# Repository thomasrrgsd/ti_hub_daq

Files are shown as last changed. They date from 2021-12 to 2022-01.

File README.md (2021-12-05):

<h1 align="center">TI Innovator HUB Data Aquisition Tool<br/>Team TI-82<br/>Cameron Dennis, John Douthit, William Jarratt, Christian Offodile</h1>

## Table of Contents

* [Introduction](#introduction)
* [User Guide and Theory of Operation](#user-guide-and-theory-of-operation)
* [Folder Descriptions](#folder-descriptions)
* [Demonstration Videos](#demonstration-videos)
* [Project Pitch](#project-pitch)

## Introduction

### Background
Students often begin learning about electronics in an environment where there is no access to the needed equipment, such as oscilloscopes, logic analyzers, function generators, and multimeters.

### Objective
Our goal was to create an inexpensive add-on for the TI Innovator HUB that provides data acquisition capabilities, with an intuitive web page based graphical user interface that works across many user devices.

### Product Requirements
- 8 Channel logic analyzer
- DMM that measures current, voltage, power, resistance
- 2 Channel oscilloscope
- Sine, square, sawtooth function generator
- Web browser-based GUI
- Wi-Fi Connectivity

### Design Challenges Encountered
- Integrating firmware for each peripheral.
- Optimizing data stream for real time operation.
- Changing firmware to allow peripherals to communicate with each other.
- Improving error checking to prevent hangups.

##  User Guide and Theory of Operation

Please see [this folder](./project_files/).

## Folder Descriptions

- /esp32_firmware: This folder gives the rundown on the wifi module (ESP32). Contains the firmware and instructions on how to upload it to the ESP32 and run it with the TI Innovator HUB.
- /final_gui: This folder shows the code behind the web based GUI. This folder contains instructions on how you can modify the webpages, encode them, and update them on the ESP32.
- /project_files: This folder contains administrative documents such as BOM, budget, project planning, theory of operation, and user manual. It is important to note that how to use the project and how it works is contained in the documents in this folder.
- /schematics: This folder contains the CAD files used to create the PCBs for each module. The PCBs were designed using EagleCAD.
- /ti_innovator_hub_firmware: This folder contains information on the firmware that resides inside the TI Innovator HUB. How the software works is located in the theory of operation document.

## Demonstration Videos

- [Beta Demo Video](https://youtu.be/WWzbL9Egt7U)
- [Final Demo Video](https://www.youtube.com/watch?v=TzPDwndSMNo)

## Project Pitch

### Background of Company: 
Global semiconductor company that designs, manufactures, tests and sells analog and embedded processing chips. Our products help our customers efficiently manage power, accurately sense and transmit data and provide the core control or processing in their designs.

### Problem Background and the need:
Work on building a basic instrumentation tool for portable signal measurements using the classroom ready TI-Innovator Hub product. Create a basic oscilloscope out of a microcontroller for collecting test and measurement data! Over the course of the project, the team will use an existing microcontroller kit and create a GUI interface to showcase wave forms, logic analyzer data, and digital multimeter functions. It is very important for engineers to be able to take measurements when debugging hardware. While benchtop equipment is highly capable, it is not portable and can be very expensive. The best tools are often the ones that are available, so portable tools are always in demand, even if the performance is not the same as professional equipment. The team will create software that works with existing hardware to display information collected from the portable data acquisition tool. They will iterate the design to improve the user “out of box” experience. They will use Whole Product development philosophy to create the necessary marketing materials and software examples to ensure a positive experience with users. The team will also design or research any accessory components that will be included in the final kit, which could include a custom enclosure, connectors, cables, power supplies, stickers, and other necessary parts.

### Problem Description/requirements (List of high-level functionality you expect to see in the end product):
- Software GUI that runs in web browser or as native PC application
- GUI Composer app or HTML5 app
- Functional prototype
- TI-Innovator Hub
- Jumper Wires
- (optional) Additional sensors or peripherals (e.g. DAC, voltmeter)
- (optional) Measurement probes or scope probes
- Programmable by USB from host PC
- Test plan to verify use for academic settings
- Identify and test use cases for basic circuits
- Documentation on user manual and quick start guide
- Include pin map diagram for inputs
- Include color photo of final board
- Explanation of out of box demo or default program
- At least 1 example code samples with documentation
- Measurements displayed in GUI
- Can be based on TI code examples provided for MCU or other sources
- Make available for Code Composer Studio and/or Arduino IDE
- Written list or physical prototypes of accessories for the development board which could include a custom enclosure, connectors, cables, power supplies, stickers, and other necessary parts

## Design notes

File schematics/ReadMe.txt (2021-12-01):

List of Files in Folder
* FUNCGEN (Function Generator hardware files)
   * FUNCGENSCH.png (Image of schematic)
   * FUNCGENBRD (Image of board layout)
   * PCB_TI82_FuncGen.zip (Gerber files)
   * TI_DAC_PCB (Eagle design files)
      * TI_DAC5V.brd (Board design file)
      * TI_DAC5V.sch (Schematic design file)
* ESPPCB1 (Wifi Module hardware files 1st iteration)
   * ESPSCH1.png (Image of schematic)
   * ESPPCB1.png (Image of board layout)
   * PCB_TI82_ESP1.zip (Gerber files)
   * TI_ESP_PCB (Eagle design files)
      * TI_ESP_PCB.brd (Board design file)
      * TI_ESP_PCB.sch (Schematic design file)
* ESPPCB2 (Wifi Module hardware files 2nd iteration)
   * ESPSCH2.png (Image of schematic)
   * ESPPCB2.png (Image of board layout)
   * PCB_TI82_ESP2.zip (Gerber files)
   * TI_ESP_PCB2 (Eagle design files)
      * TI_ESP_PCB2.brd (Board design file)
      * TI_ESP_PCB2.sch (Schematic design file)
* MULTIMETER
   * DMMSCH (Image of schematic)
   * DMMPCB (Image of board layout)
   * PCB_TI82_DMM.zip (Gerber files)
   * TI_DMM_PCB (Eagle design files)
      * TI_DMM_PCB.brd (Board design file)
      * TI_DMM_PCB.sch (Schematic design file)

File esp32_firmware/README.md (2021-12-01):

# Wifi Module (ESP32-WROOM-32D)

## Table of Contents

* [Introduction](#introduction)
* [Software](#software)
* [Hardware](#hardware)
* [How to Program using USB to TTL](#how-to-program-using-usb-to-ttl)
* [Bugs and To Do](#bugs-and-to-do)

## Introduction

The wifi Module is connected to the TI Innovator HUB using a grove cable and host the graphical user interface that the user uses from their device. The wifi module communicates over the grove cable using UART at 4Mbps. The GUI sends commands and receives data from the wifi module through 2 websockets. Websocket 1 is for commands from GUI to wifi modules and websocket 2 is for data from wifi module to GUI. The commands received from the GUI are forwarded over UART to the TI Innovator HUB. The data that is sent to the GUI comes from the TI Innovator HUB via UART.

Wifi Module High Level

## Software

The firmware was produced using the Arduino IDE. The ESP32 package may need to be installed, [Install ESP package in Arduino](https://docs.espressif.com/projects/arduino-esp32/en/latest/installing.html). The software utilizes the AsyncTCP and ESPAsyncWebServer packages that can be found at [ESPAsyncWebServer](https://github.com/me-no-dev/ESPAsyncWebServer) and [AsyncTCP github](https://github.com/me-no-dev/AsyncTCP).

The firmware can be broken down into a few parts:

1. Webpage GZIP encoded binary arrays. These can be found from line 29 to line 43 (line numbers could change). The creation of these binary arrays can found in the final_gui directory. These arrays contain the complete set of GUI information needed by the webbrowser.
2. Setup and initialization of the Async Server and websocket. The tcp server and websockets are configured to response to certain http request. Each webpage and dependency is routed to a certain http request and is configured to be transmitted using GZIP encoding. The websockets are configured to responde to certain URLs on ports 80 and 81. Also, how the websockets respond to an event is configured in onEvent and onEvent2. The websocket responses are simply to forward data to either the TI Innovator HUB or to the GUI.
3. Loop function. Inside this function, the wifi module monitors UART channel 2 for incoming data from the TI Innovator HUB. When data is found, and both websockets are open, then the HandleDataPacket function is called to handle the incoming data from the TI Innovator HUB. This data is sent to the webpage GUI through websocket 2.

## Hardware

The wifi module uses an ESP32-WROOM-32D on a customized PCB that was designed by Christian Offodile. The PCB pictured below is an earlier revision but maintains similar functionality to our final PCB design. For more information on the final PCB iteration, please look into the schematics directory. 

A.  This 2x3 male header is used by the ESP programmer [ESP-Prog-Board](https://docs.espressif.com/projects/espressif-esp-iot-solution/en/latest/hw-reference/ESP-Prog_guide.html). Alternatively, this header can be used with the pushbuttons to program the ESP32 using a USB to TTYL converter [Example](https://www.amazon.com/gp/product/B07WX2DSVB/ref=ppx_yo_dt_b_asin_title_o01_s00?ie=UTF8&psc=1).

B.  This grove connector is used to connect the Wifi PCB to the TI-Innovator HUB. The connector provides power and a connection to UART2 RX and TX.

C.  These LEDs are from top to bottom: Amber (GPIO 23), Red (GPIO 22), and Green (GPIO 21).

D.  This 3 pin male header is used to choose which power source is to be used. The jumper on the bottom 2 pins is for the programmer supplying power. The top 2 pins are for the grove connector to the TI-Innovator HUB.

E.  These 2 pushbuttons are used to pull the EN and GPIO1 low. EN and GPIO1 are normally pulled high via a pull up resistor. Pulling EN and GPIO-0 low is required to download the firmware if not using the ESP-Prog-Board, or any other programmer that has extra circuitry available to pull the EN and GPIO1 pins low. The pushbuttons were introduced to allow for wider compatibility with programmers.

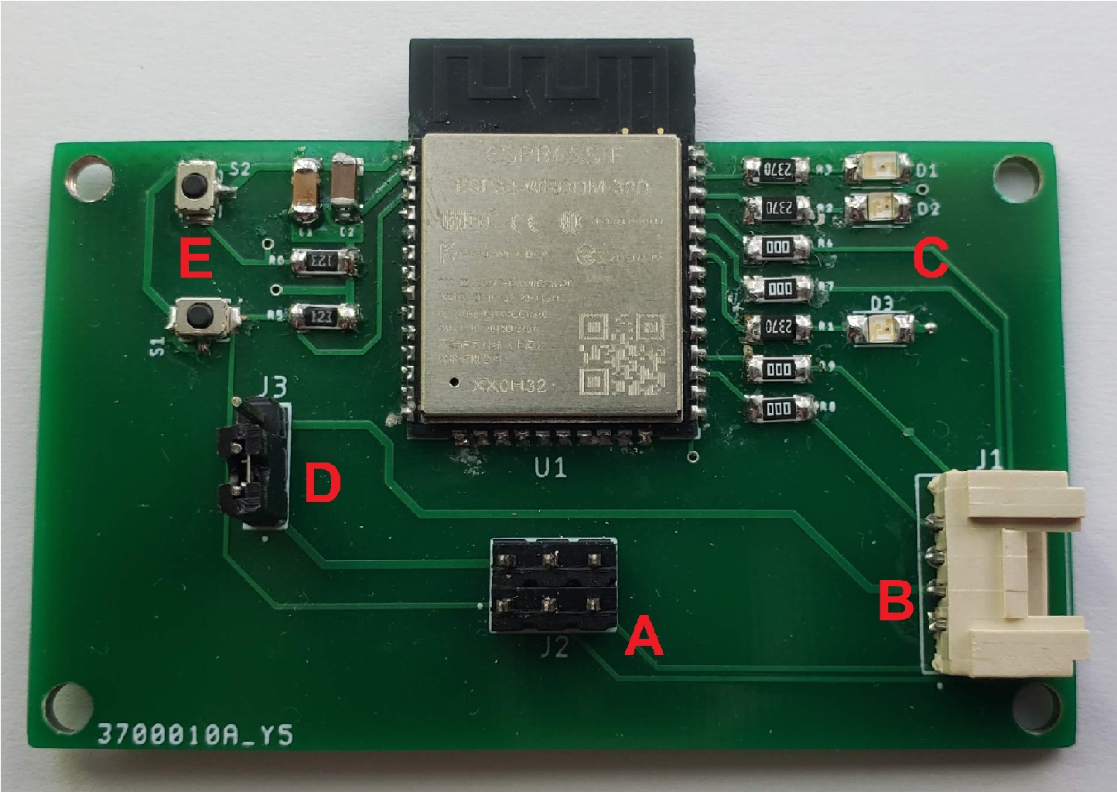
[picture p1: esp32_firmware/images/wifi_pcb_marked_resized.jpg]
wifi_pcb


## How to Program Using USB to TTL

### **Some programmers can be configured for 5v. Ensure that it is not set to 5v. The PCB does not step down the voltage.**

These steps are for those who are using a USB to TTL programmer that does not have a circuit available for pulling EN and GPIO1 low.

1. Arduino IDE and programmer are installed and configured. Arduino has all necessary dependencies installed and programmer has drivers installed.
2. Close any application on your computer that uses the USB to TTL programmer. The UART channel 0 cannot be shared.
3. Apply power (3v3) to the ESP32 via a power source that can provide > 250 mA @ 3v3. The TI Innovator HUB has 3v3 available with max amperage of 500 mA available on the breadboard.
4. Connect ESP32 UART0 TX to programmer RX, connect ESP32 UART0 RX to programmer TX.
5. Ensure that programmer and ESP32 share the same ground reference. Connect programmer ground to ESP32 ground.
6. Determine which COM port the programmer uses and set the Arduino IDE to use that COM port.
7. Begin upload of sketch to ESP32 from Arduino IDE. You will see a message showing that the Arduino IDE is trying to program the ESP32. You will see "___...". At this point you must press the pushbotton that pulls GPIO1 low. Hold that pushbutton until the download begins.
8. Once the download has finished, press the pushbotton that pulls EN low to reset the ESP32. 
9. Once the ESP32 is reset it should begin running the firmware downloaded to it.

Note: You can use a serial terminal, such as [Tera Term](https://ttssh2.osdn.jp/index.html.en) to view what is happening on UART channel 0 using the USB to TTL programmer, while you are not downloading firmwares. For example, if you hold GPIO1 low and press reset, you will see in the serial terminal that the ESP32 goes into serial bootloader mode.

## Bugs and To Do

### To Do
- Add admin page: We want the user to be able to set the SSID and password among other properties. These properties can be stored in static memory and kept after power down and reset.
- Add randomized SSID: Because there will be multiple devices running, the SSIDs cannot collide and so we can use the ESP32 unique MAC address to achieve this.
- Increase operation robustness: As of now, the wifi module operates well, and most hangups result from the TI Innovator HUB. However, the ESP32 has cpu resources that could be dedicated to error checking and handling to help with hangups caused anywhere in the data streaming pipeline.

### Bugs
- The websocket hangs up and quick data speeds. It is suspected that this may have something to do with the buffer. Making the device operation more robust would include adding ways of checking and handling buffer overflow.

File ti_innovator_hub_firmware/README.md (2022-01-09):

# TI Innovator HUB Firmware (MSP432P401R)

## Table of Contents

* [Introduction](#introduction)
* [Software](#software)
* [Hardware](#hardware)
* [Bugs and To Do](#bugs-and-to-do)

## Introduction

The TI Innovator HUB is the center of this project. Each module connects to the HUB through its many grove ports described in the [Hardware](#hardware) section. When the HUB is powered on, it intializes all its peripherals and configures the multimeter. Then it runs in a loop where it waits for incoming serial data from the wifi module. When a command is given, the HUB responds. When a module is turned on (e.g. Oscilloscope), then the data is recorded and turned into a data packet. This data packet is updated and sent out to the wifi module repeatedly in the loop. The HUB is always communicating with the wifi module, but if nobody is connected to the wifi, then the data is just dumped in the wifi module.

## Software

The firmware for the TI Innovator HUB was written with Code Composer Studio (CCS) 10.4. This project uses software abstraction layers from the driverlib package. The project requires [driverlib](https://www.ti.com/tool/MSPDRIVERLIB) to run. Addtionally, the TI Innovator HUB contains an MSP432P401R and so in order to flash the HUB, you must have the MSP432 drivers installed.
It is intended that the CCS project files will be converted into a TI Innovator HUB sketch in the future to allow flashing with the sketch using the appropriate tool. The firmware utilizes many of the HUBs internal peripherals to perform its functions. The UART, I2C, DMA, ADC, TIMER_A, and Interrupt vectors are used. The theory of operation is not covered here, but is instead found in the [project_files folder](https://github.com/thomasrrgsd/ti_hub_daq/tree/main/project_files).

## Hardware

The TI Innovator HUB has an MSP432P401R inside of it and this was used to prototype the TI Innovator HUB DAQ. The TI Innovator HUB documentation specifies how the port pins are mapped to the external connectors. The pin mappings are given below in addition with there function with regard to the project:
- IN1 / P5.4 and P5.5 / Not used
- IN2 / P4.5 and P4.7 / A8 and A6 (Oscilloscope ch 2 and 1 respectively)
- IN3 / P4.4 / Not used
- OUT1 / P3.2 and P3.3 / Wifi module UART RX and TX
- OUT2 / P3.5 and P3.7 / Not used
- OUT3 / Power input for wifi module
- I2C / P6.4 and P6.5 / Multimeter and Function Generator
- Breadboard / {P2.6, P2.4, P2.7, P5.1, P5.2, P5.0, P3.0, P1.5, P1.6, P1.7} / Logic Analyzer channels 1-8.

Additionally, you can look at the firmware to see which pins are mapped to which device.

## Bugs and To Do

### To Do
- Fix magic numbers: There are numbers in the code that represent something but are not obvious do to not using obvious names.
- Update variable types to uint8_t and uint16_t, etc: For uniformity and also to make sure that code is compatible between different devices if needed. Only important in the case where a variable, such as int is a different size on different devices.
- Increase robustness of firmware: The firmware doesn't operate as efficient as it could. Some areas of code rely on time delays. There are bugs that can hang up the system and requires a restart. Some issues can be solved by implementing more error checking to increase robustness.
- Increase modularity and minimize use of global variables: We want each peripheral and module to have its own .c and .h file. This provides a nice API that abstracts and simplifies coding as the project becomes more complex (it got very complex). Additionally, not protecting code and using bad practices, such as global variables can easily cause or be the cause of bugs due to uncoordinated access to a global variable.
- Switch firmware to RTOS: Right now we have to use delays to make the modules operate together. A robust system for coordinating operation is needed. This can be best provided by an RTOS.
- Change I2C to DMA: Interrupts introduce tremendous overhead. This is a significant overhead with regards to the function generator.

### Bugs

- Without a delay after initialization in main, the firmware does not operate correctly when not in debug mode. Most likely due to the I2C not being ready before initializing the multimeter directly after enabling interrupts.
- When receiving serial data (command packet) on UART2 RX, sometimes the data will be dropped and hangup the serial data stream. This began happening when the baud rate was increased to 4Mbps. We knew that raising the baud this high would introduce errors and there is no existing system to account for this error. This is one major reason for using time delays to send information. Ideally, the GUI or ESP32 would notify the MSP432 when it can send its next data, but every so often it hangs up without error checking. On a period delay, if data is missed, then it just keeps going.
- Multimeter and Function Generator must be plugged into I2C for the project to work. This is due to using a while loop with the multimeter and function generator I2C code that looks for a successful transmit. If the transmit does not succeed, then the program hangs up. There are better ways to implement this system and we just did not have time to get around to it.

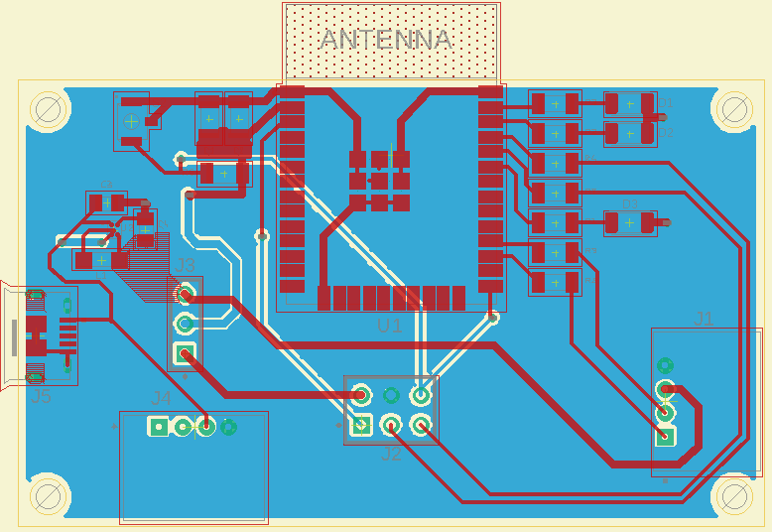
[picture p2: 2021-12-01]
schematics/ESPPCB2/ESPPCB2.png

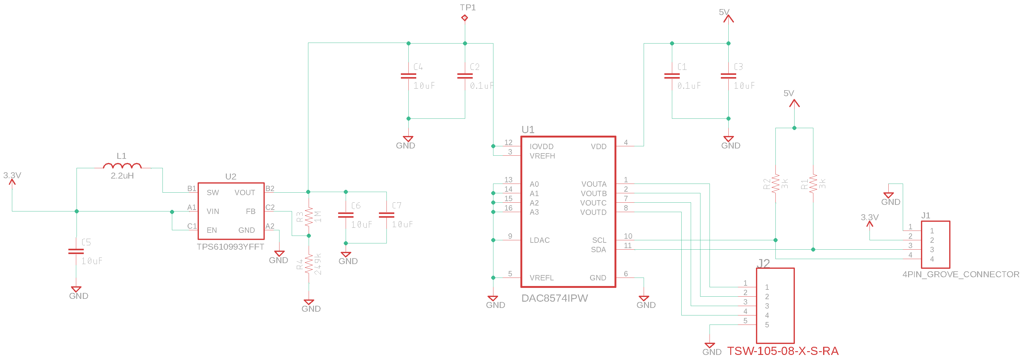
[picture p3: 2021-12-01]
schematics/FUNCGEN/FUNCGENSCH.png

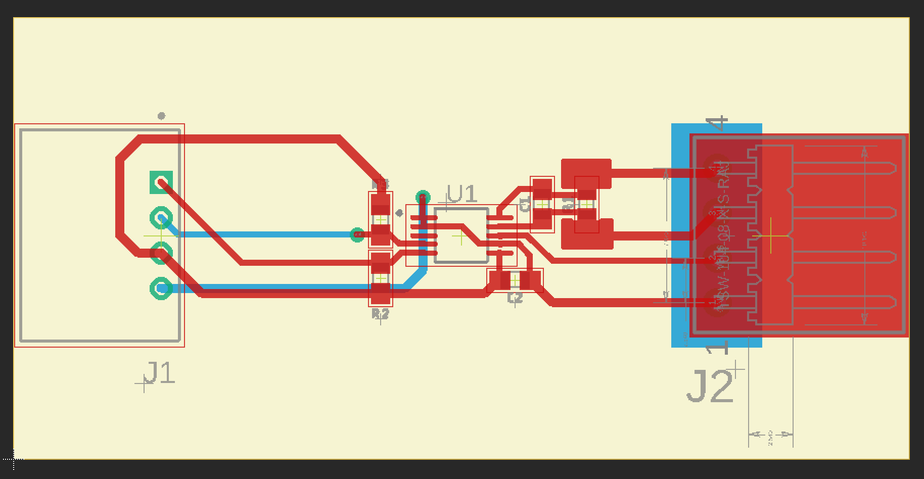
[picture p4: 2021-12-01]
schematics/MULTIMETER/DMMPCB.png

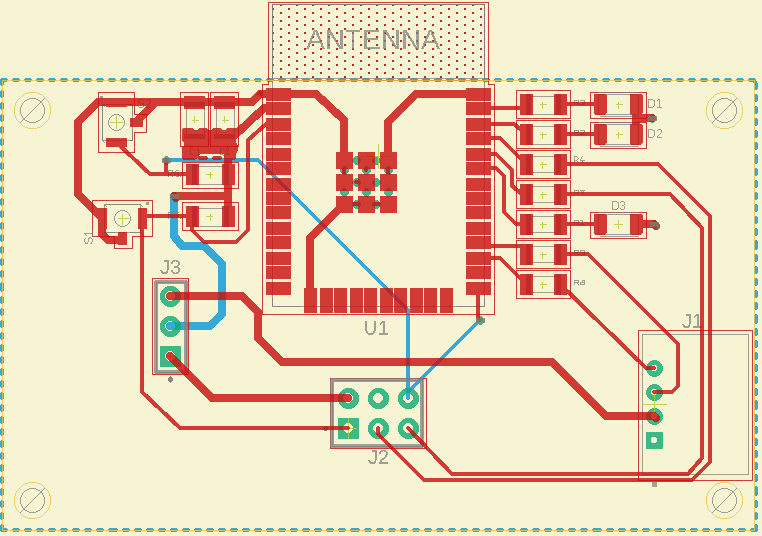
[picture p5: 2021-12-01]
schematics/ESPPCB1/ESPPCB1.png

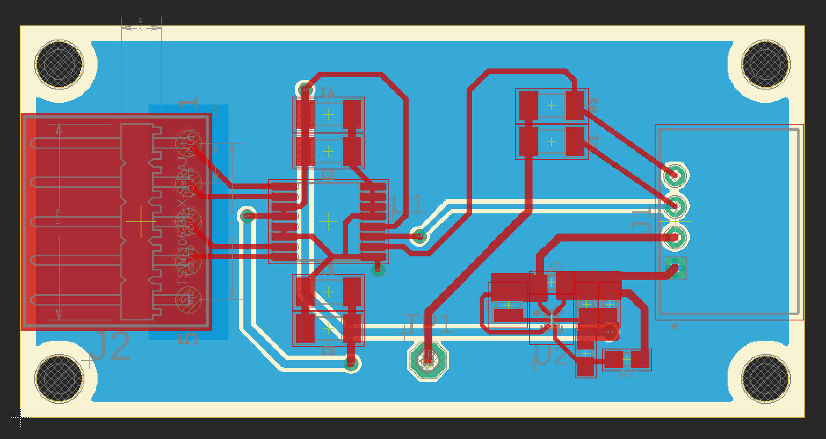
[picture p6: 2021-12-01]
schematics/FUNCGEN/FUNCGENBRD.png

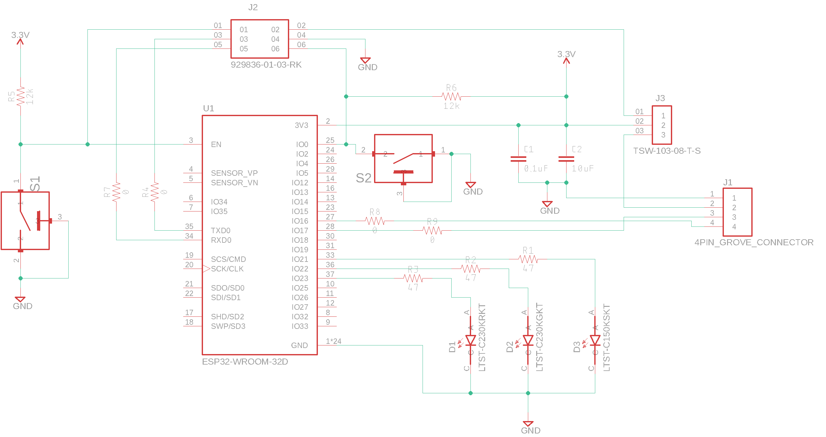
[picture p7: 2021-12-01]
schematics/ESPPCB1/ESPSCH1.png

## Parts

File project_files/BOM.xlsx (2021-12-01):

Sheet: BOM
Function Generator Parts List
QUANTITY | MANUFACTURER PART NUMBER | COMMENT | DESIGNATOR | FOOTPRINT | UNIT PRICE ($) | EXTENDED PRICE ($) | NOTES
1 | TSW-105-08-T-S-RA (https://www.digikey.com/en/products/detail/TSW-105-08-T-S-RA/SAM1051-05-ND/1102419?itemSeq=380598215) | CONN HEADER R/A 5POS 2.54MM | J2 | -- | 0.42 | 0.42
1 | 114020163 (https://www.digikey.com/en/products/detail/seeed-technology-co.,-ltd/114020163/12323560) | Grove Series Connector 20 Pack | J1 | -- | 3.2 | 3.2
2 | C1206C104K8RAC7800 (https://www.digikey.com/en/products/detail/kemet/C1206C104K8RAC7800/2215080?s=N4IgTCBcDaIMIEYwAYBsjkBYDSAOASgIJwDsuyyIAugL5A) | CAP CER 0.1UF 10V X7R 1206 | C1, C2 | 1206 | 0.45 | 0.9
2 | C1206C106K8PACTU (https://www.digikey.com/en/products/detail/kemet/C1206C106K8PAC7800/2215117?s=N4IgTCBcDaIMIEYwAYBsi0GkAcAFAgnACoCqIAugL5A) | CAP CER 10UF 10V X5R 1206 | C3, C4 | 1206 | 0.36 | 0.72
2 | GRM188R60J106ME47J (https://www.digikey.com/en/products/detail/GRM188R60J106ME47J/490-6405-1-ND/3845602?itemSeq=375936658) | CAP CER 10UF 6.3V X5R 0603 |  | 603 | 0.37 | 0.74
2 | ERJ-8GEYJ302V (https://www.digikey.com/en/products/detail/panasonic-electronic-components/ERJ-8GEYJ302V/2226?s=N4IgTCBcDaIKICUBSBaAHAcTgTSQZgAYwA1EAXQF8g) | RES SMD 3K OHM 5% 1/4W 1206 | R1, R2 | 1206 | 0.14 | 0.28
1 | VLS201610CX-2R2M-1 (https://www.digikey.com/en/products/detail/tdk-corporation/VLS201610CX-2R2M-1/5169756) | 2.2 µH Inductor 1.53 A 163mOhm | L1 | Nonstandard | 0.43 | 0.43
1 | RC0603FR-071ML (https://www.digikey.com/en/products/detail/yageo/RC0603FR-071ML/726844?s=N4IgTCBcDaIEoGEAMA2JBmAYnAtEg7AIwCyAMiALoC%2BQA) | RES SMD 1M OHM 1% 1/1W 0603 | R3 | 603 | 0.1 | 0.1
1 | CRCW0603249KFKEB (https://www.digikey.com/en/products/detail/vishay-dale/CRCW0603249KFKEB/11501171) | RES SMD 249K OHM 1% 1/10W 0603 | R4 | 603 | 0.1 | 0.1
1 | TPS61099YFFR (https://www.digikey.com/en/products/detail/texas-instruments/TPS61099YFFR/6207348?s=N4IgTCBcDaICoAUDKA2AjABgJxYJoDF8AlEAXQF8g) | Boost Switching Regulator | U2 | 6-DSBGA | 2.02 | 2.02
1 | DAC8574IPW (https://www.digikey.com/en/products/detail/texas-instruments/dac8574ipwr/1509359) | Digital to Analog Converter | U1 | 16TSSOP |  | 0
Multimeter Parts List
1 | INA226AIDGSR (https://www.ti.com/product/INA226?ds_k=INA226&DCM=yes&gclsrc=aw.ds) | INA226 | U1 |  | 1.26 | 1.26
1 | ERJ-3RSJR10V (https://www.digikey.com/en/products/detail/panasonic-electronic-components/ERJ-3RSJR10V/308026) | RES SMD 0.1 OHM 5% 1/10W 0603 | R1 | 603 | 0.23 | 0.23
2 | RC1608J103CS (https://www.digikey.com/en/products/detail/samsung-electro-mechanics/RC1608J103CS/3965393?s=N4IgTCBcDaIEoGECMA2ADADgFJLQZgQGUQBdAXyA) | RES SMD 10K OHM 5% 1/10W 0603 | R2, R3 | 603 | 0.1 | 0.2
1 | 0603YC104JAT2A (https://www.digikey.com/en/products/detail/kyocera-avx/0603YC104JAT2A/1116252?s=N4IgTCBcDaIAwDY4GYCaBhAjHALAKQEEAVMAkAXQF8g) | CAP CER 0.1UF 16V X7R 0603 | C1, C2 | 603 | 0.12 | 0.12
1 | TSW-104-08-T-S-RA (https://www.digikey.com/en/products/detail/samtec-inc/TSW-104-08-T-S-RA/1102420) | CONN HEADER R/A 4POS 2.54MM | J2 | -- | 0.34 | 0.68
1 | 114020163 (https://www.digikey.com/en/products/detail/seeed-technology-co.,-ltd/114020163/12323560) | Grove Series Connector 20 Pack | J1 | -- | 3.2 | 3.2
ESP32 Parts List
1 | ESP32-WROOM-32D (https://www.digikey.com/en/products/detail/espressif-systems/ESP32-WROOM-32D-4MB/9381716) | ESP32-WROOM-32D (4MB) | U1 | -- | 4.08 | 4.08
2 | B3U1100P (https://www.digikey.com/en/products/detail/omron-electronics-inc-emc-div/B3U-1100P/1534339) | SWITCH TACTILE SPST-NO 0.05A 12V | S1, S2 | -- | 0.96 | 1.92
2 | C1206C104K8RAC7800 (https://www.digikey.com/en/products/detail/kemet/C1206C104K8RAC7800/2215080?s=N4IgTCBcDaIMIEYwAYBsjkBYDSAOASgIJwDsuyyIAugL5A) | CAP CER 0.1UF 10V X7R 1206 | C1 | 1206 | 0.45 | 0.9
2 | C1206C106K8PACTU (https://www.digikey.com/en/products/detail/kemet/C1206C106K8PAC7800/2215117?s=N4IgTCBcDaIMIEYwAYBsi0GkAcAFAgnACoCqIAugL5A) | CAP CER 10UF 10V X5R 1206 | C2 | 1206 | 0.36 | 0.72
1 | 114020163 (https://www.digikey.com/en/products/detail/seeed-technology-co.,-ltd/114020163/12323560) | Grove Series Connector 20 Pack | J1, J4 | -- | 3.2 | 3.2
2 | 929836-01-03-RK (https://www.digikey.com/en/products/detail/3m/929836-01-03-rk/2184030) | CONN HEADER VERT 6POS 2.54MM | J2 | -- | 0.46 | 0.92
2 | TSW-103-08-T-S (https://www.digikey.com/en/products/detail/samtec-inc/TSW-103-08-T-S/1102371) | CONN HEADER VERT 3POS 2.54MM | J3 | -- | 0.25 | 0.5
4 | ERJ-8GEY0R00V (https://www.digikey.com/en/products/detail/panasonic-electronic-components/ERJ-8GEY0R00V/27495?s=N4IgTCBcDaIKICUBSBaAHAcTgTQAwN1wDUQBdAXyA) | RES SMD 0 OHM JUMPER 1/4W 1206 | R4, R7, R8, R9 | 1206 | 0.1 | 0.4
0 | ERJ-8GEYJ471V (https://www.digikey.com/en/products/detail/panasonic-electronic-components/ERJ-8GEYJ471V/17184) | RES SMD 470 OHM 5% 1/4W 1206 | R4, R7, R8, R9 | 1206 | 0.1 | 0
2 | ERJ-8GEYJ123V (https://www.digikey.com/en/products/detail/panasonic-electronic-components/ERJ-8GEYJ123V/14294) | RES SMD 12K OHM 5% 1/4W 1206 | R5, R6 | 1206 | 0.1 | 0.2
1 | LTST-C230KRKT (https://www.digikey.com/en/products/detail/lite-on-inc/LTST-C230KRKT/386857?s=N4IgTCBcDaIDIBUDKCC0BhMBmADAaQCU8EQBdAXyA) | LED RED CLEAR CHIP SMD | D1 | 1206 | 0.31 | 0.31
1 | LTST-C230KGKT (https://www.digikey.com/en/products/detail/lite-on-inc/LTST-C230KGKT/386855?s=N4IgTCBcDaIDIBUDKCC0BhMBmADAaQHE8EQBdAXyA) | LED GREEN CLEAR CHIP SMD | D2 | 1206 | 0.31 | 0.31
1 | LTST-C150KSKT (https://www.digikey.com/en/products/detail/lite-on-inc/LTST-C150KSKT/386763?s=N4IgTCBcDaIDIBUDKCC0BhAjAVgAwGkl8EQBdAXyA) | LED YELLOW CLEAR CHIP SMD | D3 | 1206 | 0.35 | 0.35
1 | ERJ-8GEYJ470V (https://www.digikey.com/en/products/detail/panasonic-electronic-components/ERJ-8GEYJ470V/15762?s=N4IgTCBcDaIKICUBSBaAHAcTgTSQFgHYAGANRAF0BfIA) | RES SMD 47 OHM 5% 1/4W 1206 | R1 | 1206 | 0.1 | 0.1
1 | ERJ-8GEYJ470V (https://www.digikey.com/en/products/detail/panasonic-electronic-components/ERJ-8GEYJ470V/15762?s=N4IgTCBcDaIKICUBSBaAHAcTgTSQFgHYAGANRAF0BfIA) | RES SMD 47 OHM 5% 1/4W 1206 | R2 | 1206 | 0.1 | 0.1
1 | ERJ-8GEYJ470V (https://www.digikey.com/en/products/detail/panasonic-electronic-components/ERJ-8GEYJ470V/15762?s=N4IgTCBcDaIKICUBSBaAHAcTgTSQFgHYAGANRAF0BfIA) | RES SMD 47 OHM 5% 1/4W 1206 | R3 | 1206 | 0.1 | 0.1
1 | LM3671TL-3.3/NOPB (https://www.digikey.com/en/products/detail/texas-instruments/LM3671TL-3-3-NOPB/1590065) | IC REG BUCK 3.3V 600MA 5DSBGA | U2 | 5DSBGA | 1.67 | 1.67
1 | 10118194-0001LF (https://www.digikey.com/en/products/detail/amphenol-icc-fci/10118194-0001LF/2785389?s=N4IgTCBcDaIGwAYCcAWOBGAHOgcgERAF0BfIA) | USB - micro B USB 2.0 Receptacle Connector 5 Position Surface Mount, Right Angle; Through Hole | J5 |  | 0.45 | 0.45
1 | CDRH2D14NP-2R2NC (https://www.digikey.com/en/products/detail/sumida-america-components-inc/CDRH2D14NP-2R2NC/2108186?s=N4IgTCBcDaIMIBEBKAJMCCMAWAcgBQFowkwc4QBdAXyA) | FIXED IND 2.2UH 1.6A 94 MOHM SMD | L1 | Nonstandard | 1.08 | 1.08
1 | JMK212BJ475KG-T (https://www.digikey.com/en/products/detail/taiyo-yuden/JMK212BJ475KG-T/930654) | CAP CER 4.7UF 6.3V X5R 0805 |  | 805 | 0.19 | 0.19
1 | C2012X5R0J106K085AB (https://www.digikey.com/en/products/detail/tdk-corporation/C2012X5R0J106K085AB/2733109) | CAP CER 10UF 6.3V X5R 0805 |  | 805 | 0.29 | 0.29

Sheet: Project Budget
The tech demo uses evaluation kits to show functionality. The final cost was $310.40 with the W600 Wifi Module. The final prototype replaces evaluation kits with designed PCBs and components and uses the TI-Innovator Hub to show functionality. The final cost is $216.85 with the W600 Wifi Module.
Description | Part Number | Supplier | Use | Cost per Unit | Units | Total Cost | Comments
Tech Demo
PCB - Multi-meter |  |  | PCB for multimeter | $5.00 | 1 | $5.00
PCB - Function Generator |  |  | PCB for function generator | $5.00 | 1 | $5.00 | Add 5 for WIFI PCB if using CC3120
MSP432P401R LaunchPad | MSP-EXP432P401R | Texas Instruments | Simulates TI Hub, has Logic Analyzer and Oscilloscope | $42.00 | 1 | $42.00
Voltage/Current Monitor | IMETER-BOOST | Texas Instruments | Prototype DMM | $20.00 | 1 | $20.00
DAC8574 Evaluation Module | DAC8574EVM | Texas Instruments | Prototype Function Generator | $49.00 | 1 | $49.00
Grove Starter Kit for LaunchPad | GROVESTARTKIT | SeeedStudio | Prototype grove connects to MSP-432P401R | $59.00 | 1 | $59.00
TI-Innovator Breadboard Pack | INNOVATBREADBOARD | Texas Instruments | Breadboard and components needed for prototyping. | $40.50 | 1 | $40.50
Sidekick Basic Kit for TI LaunchPad | SIDEKICKBASIC | SeeedStudio | Allows for easier prototyping between TI LauchPad and breadboard. | $30.00 | 1 | $30.00
Wifi-Module (pick one)
- UART Wifi V2 (ESP8285 | SKU 113020011 | SeeedStudio | Complete Wifi module. | $13.90 | 1 | $13.90
- DOIT DEVIT V1 ESP32-WROOM-32 Development Board | DOIT DEVIT V1 ESP32-WROOM-32 | Amazon | DevBoard WiFi module | $16.00 | 1 | $16.00
- CC3120MOD BoosterPack | BOOSTXL-CC3120MOD | Texas Instruments | Wifi launchpad plug in module. | $30.00 | 1 | $30.00
TI Code Composer Studio |  | Texas Instruments | Program DAQ | $0.00 | 1 | $0.00
Computer |  | On-Hand | Program DAQ, access GUI | $0.00 | 1 | $0.00
 |  |  |  | Total: |  | $310.40
Final Prototype
TI - Innovator Hub w/ LaunchPad Board | TI-STEM | Calculators, INC. | Another form of the MSP432x | $75.00 | 1 | $75.00
PCB - Multi-meter |  |  | PCB for multimeter | $12.00 | 1 | $12.00
PCB - Function Generator |  |  | PCB for function generator | $12.00 | 2 | $24.00
PCB - Wifi-Module |  |  | PCB for wifi module | $12.00 | 1 | $12.00 | Add if using CC3120 or ESP32
DAC | DAC8574IPW | Texas Instruments | Digital to analog converter | $14.50 | 1 | $14.50
INA | INA226AIDGST | Texas Instruments | I2C output current/voltage/power monitor. | $1.40 | 1 | $1.40
TI-Innovator Breadboard Pack | INNOVATBREADBOARD | Texas Instruments | Breadboard and components needed for prototyping. | $40.50 | 1 | $40.50
Wifi-Module (pick one)
- UART Wifi V2 (ESP8285) | SKU 113020011 | SeeedStudio | Complete Wifi module. | $13.90 | 1 | $13.90
- ESP32-WROOM-32D | ESP32-WROOM-32D | Amazon |  | $5.00 | 5 | $25.00
- W600 | SKU 113020031 | SeeedStudio | Complete Wifi module. | $0.00 | 1 | $0.00
- CC3120MOD Wifi Chip | CC3120MODRNMMOBR | Texas Instruments | Wifi chip, no pcb. | $7.30 | 1 | $7.30
Misc. Components |  | Misc. | Resistors, capacitors, etc.
Grove 4-pin Cable (5) | 1597-1085-ND | Digi-Key | Connect modules | $1.90 | 1 | $1.90
TI Code Composer Studio |  | Texas Instruments | Program DAQ | $0.00 | 1 | $0.00
Computer |  | On-Hand | Program DAQ, access GUI | $0.00 | 1 | $0.00
 |  |  |  | Total: |  | $227.50

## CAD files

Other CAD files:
ti_innovator_hub_firmware/ti_hub_daq_2021-11-29/Debug/ccs/startup_msp432p401r_ccs.obj

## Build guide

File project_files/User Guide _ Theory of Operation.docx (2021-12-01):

# TI-Innovator Hub Data Acquisition Tool

1. User Guide 2

1.1. Introduction 2

1.2. Getting Started: Setup TI Innovator Hub 2

1.4. Connecting the Modules 4

1.3.1. Wifi Module 4

1.3.2. Multimeter and Function Generator Module 4

1.3.3. Oscilloscope Module 5

1.3.4. Logic Analyzer Module 5

1.4. Power On 6

1.5. Connecting to the Wireless Access Point 6

1.6. Running the Graphical User Interface 7

1.6.1. Multimeter 7

1.6.2. Oscilloscope 8

1.6.3. Function Generator 9

1.6.4. Logic Analyzer 9

1.7. Data Acquisition: Multimeter 10

1.8. Data Acquisition: Oscilloscope 10

1.9. Data Acquisition: Logic Analyzer 11

1.10. Driving a Circuit: Function Generator 11

2. Additional Setup for Prototype (For Mark) 13

2.1. Introduction 13

2.2. Setting up ESP32 Firmware (Arduino) 13

2.3. Setting up MSP432P401R Firmware (Code Composer Studio) 16

# 1. User Guide

## 1.1. Introduction

The TI Innovator Hub Data Acquisition Tool is a student and hobbyist level device equipped with a multimeter, a two-channel oscilloscope, an eight-channel logic analyzer, and a four-channel function generator. These modules allow a user to develop and debug entry and intermediate level circuits as they explore the fundamentals of Electrical and Computer Engineering. This kit is an add-on to the already existing TI Innovator Hub.

## 1.2. Getting Started: Setup TI Innovator Hub

1. Ensure you have all the necessary components. You will need a:
  a. microUSB cable

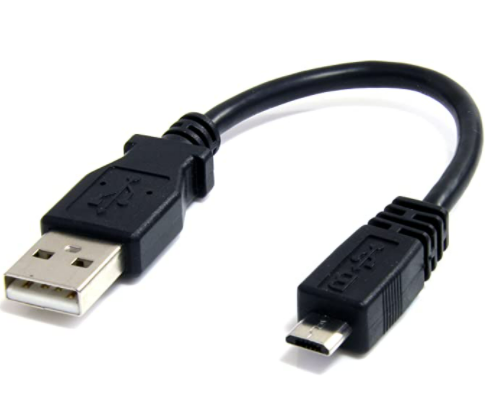
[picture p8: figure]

  b. TI Innovator Hub

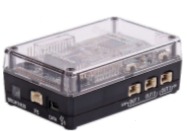
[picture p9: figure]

  c. computer with a web browser.
  d. wifi module

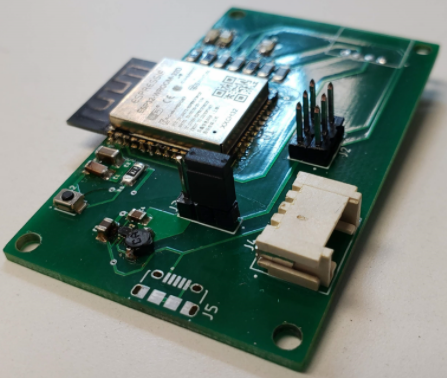
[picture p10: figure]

  e. multimeter module

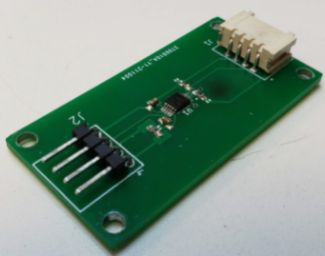
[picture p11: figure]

  f. function generator module

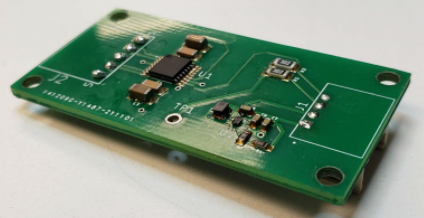
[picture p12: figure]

  g. grove module hub
  h. four female to female grove cables

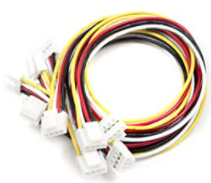
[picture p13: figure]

  j. one breadboard connector to female grove cable

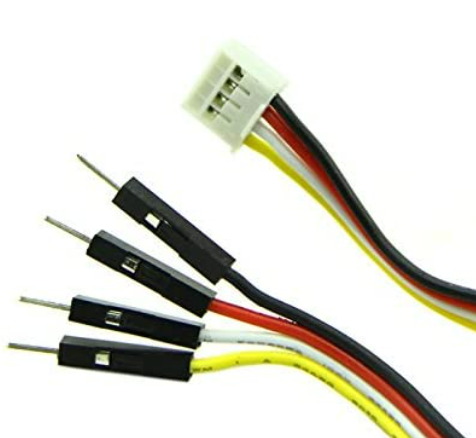
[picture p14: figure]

  k. circuit you wish to measure and breadboard wires.
2. If your TI Innovator Hub does not already have the sketch needed for the modules, please download and flash the TI Innovator Hub with the proper sketch. (This sketch does not exist at the moment) The default sketch on the TI Innovator Hub is not the correct sketch. For those needing to use Arduino and Code Composer Studio, please refer to 2. Additional Setup for Prototype. The TI software needed to update the sketch can be found at this link (https://education.ti.com/en/software/details/en/EFD1D3762FE941FAA21E774D8520AEF0/TI-Innovator_Hub_Update_SWti).
3. Once the TI Innovator Hub has the correct sketch, leave it unplugged and move on to the next section.

## 1.4. Connecting the Modules

Refer to the images below to properly connect the modules.

### 1.3.1. Wifi Module

The wifi module uses a female to female grove cable and is connected to the OUT1 port.

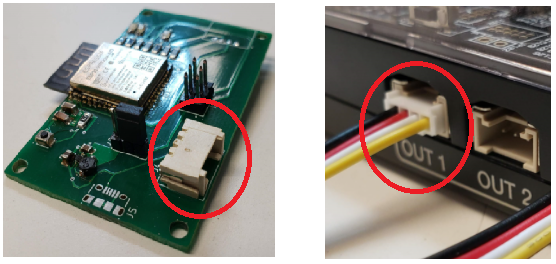
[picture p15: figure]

### 1.3.2. Multimeter and Function Generator Module

The multimeter module and function generator must be connected to the grove connector hub and the grove connector hub connected to the I2C port. These devices use female to female grove connectors.

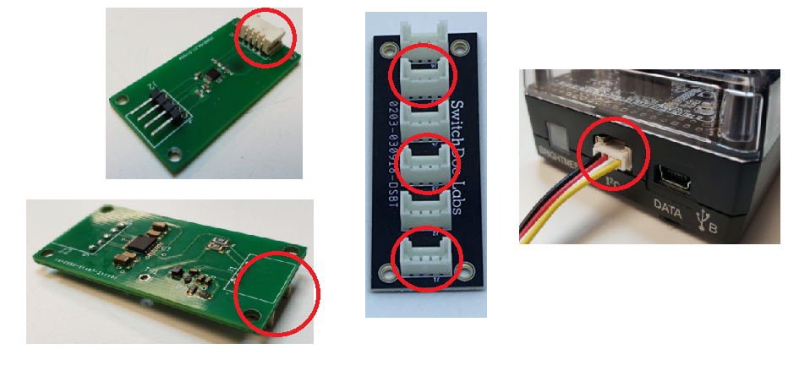
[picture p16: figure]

### 1.3.3. Oscilloscope Module

The oscilloscope does not use an external module. Instead, connect the breadboard to female grove cable into the IN2 port.

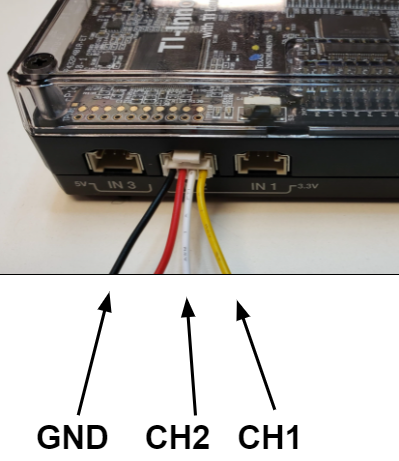
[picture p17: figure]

### 1.3.4. Logic Analyzer Module

Like the oscilloscope, the logic analyzer does not use an external module. Instead, you will connect to the logic analyzer using breadboard wires to the breadboard area of the TI Innovator Hub. Pins 1-8 are logic analyzer channels 1-8 and are referenced to the TI Innovator Hub ground.

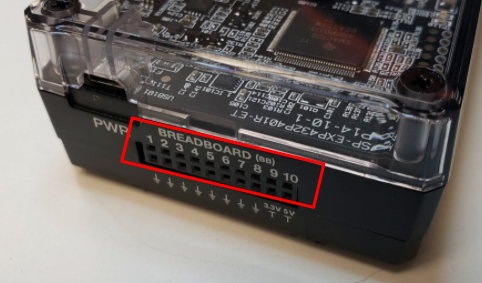
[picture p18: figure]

Once you have connected all the modules, you are ready to power on the device.

## 1.4. Power On

1. Connect the microUSB into the PWR port of the TI Innovator Hub.

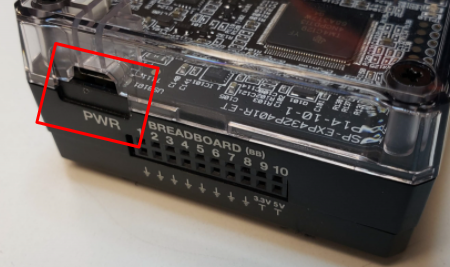
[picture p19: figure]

The microUSB cable can be connected to either a power brick or a computer USB port. If you plan to operate a circuit using the 3V3 or 5V breadboard connections that draws more than 200 mA, you will need to connect to a power brick from a wall socket.

2. You should see a red light on the TI Innovator Hub and after approximately five seconds you should see the green LED on the wifi module light up.
3. Note: If the multimeter or function generator module must be connected when power is applied.
4. You should now see a wifi connection called “ti82-team-12”.

Now that the device is powered on and ready to use, we will connect to the wifi access point provided by the wifi module.

## 1.5. Connecting to the Wireless Access Point

1. Go to your list of available wifi connections and look for “ti82-team-12”.
2. Click connect and type in the password “thisispassword”.
3. Wait for the computer to finish checking the connection. When you see “No Internet, secured”, you are ready to open the graphical user interface.

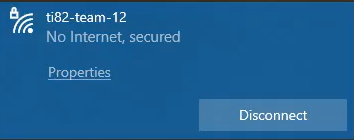
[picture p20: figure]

4. Open up a web browser and type in “daq.loca/” into the url bar. Hit enter and the graphical user interface should load.

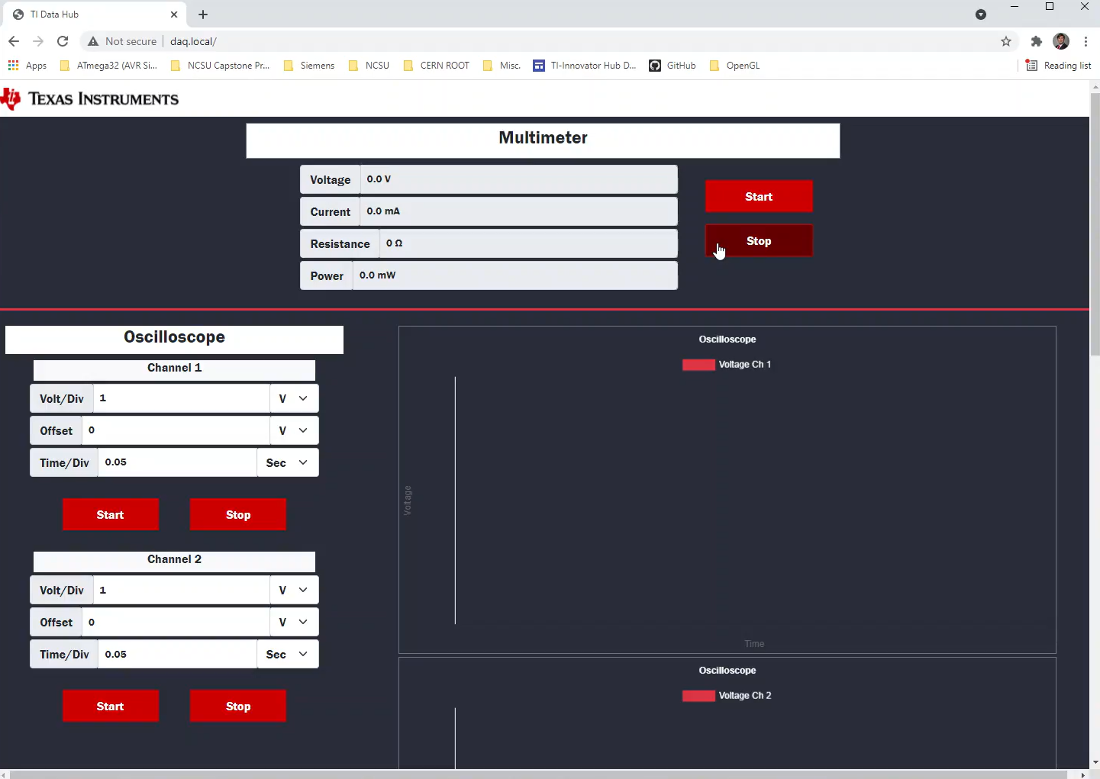
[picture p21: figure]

Now that the GUI is loaded, we will walk through the operation of the GUI.

## 1.6. Running the Graphical User Interface

### 1.6.1. Multimeter

The operation of the multimeter is fairly simple, press start to begin taking measurements and press stop to stop taking measurements. The multimeter only updates one value at a time and there is a delay between when the value changes and when it is accurately displayed in the GUI. The resistance is the only thing that is not directly measured by the multimeter and is described in a later section.

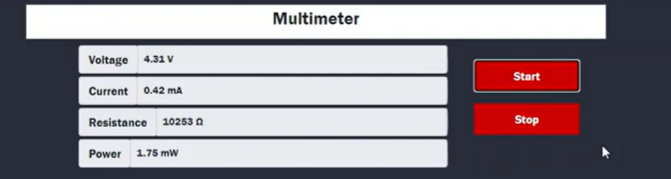
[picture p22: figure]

### 1.6.2. Oscilloscope

You can start and stop each channel of the oscilloscope independently. For each channel you can select the voltage per division, voltage offset, and time per division by typing the number into the text fields and pressing enter. The time per division is currently buggy and so only use values around 0.05 seconds per division. Though other values are possible, using too high or low a value may cause a hangup.

There are always 10 tick marks on the voltage axis. The volt/div sets the voltage per every two tick marks. The offset shifts the chart either up or down. This allows you to change the plot in a way to allow for viewing many different sizes of waveforms. Time per division changes the scaling of the time axis.

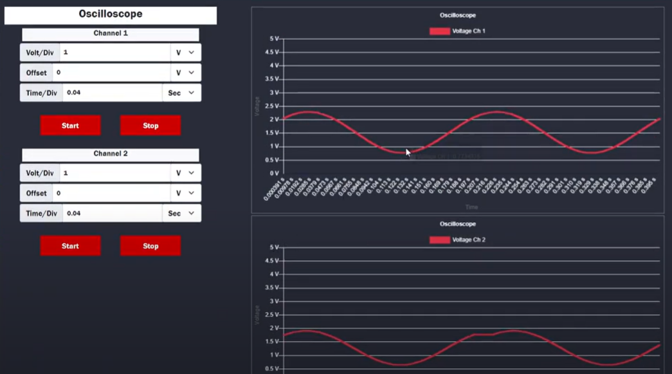
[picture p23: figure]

### 1.6.3. Function Generator

The function generator has four channels available for use. Only one channel can be used at a time and it is planned to implement all four channels in future updates.

- Channel selects which channel is active and which pin has the voltage coming out of it.
- Type allows you to select between four different waveforms: square, sine, sawtooth, and DC.
- Frequency changes the frequency of the waveform.
- Amplitude changes the peak to peak voltage of the waveform.
- Bias changes the voltage offset of the middle of the waveform.

For example, a sine wave with an amplitude of 1V and with a bias of 1V would produce a sine wave that oscillates from 0.5 to 1.5V.

When you change channels, the previous channel settings are saved. Whenever a change is made to the waveform, you must press start to update the signal. For example, if you change the type from square to sine, it will not output a sine wave until you press start.

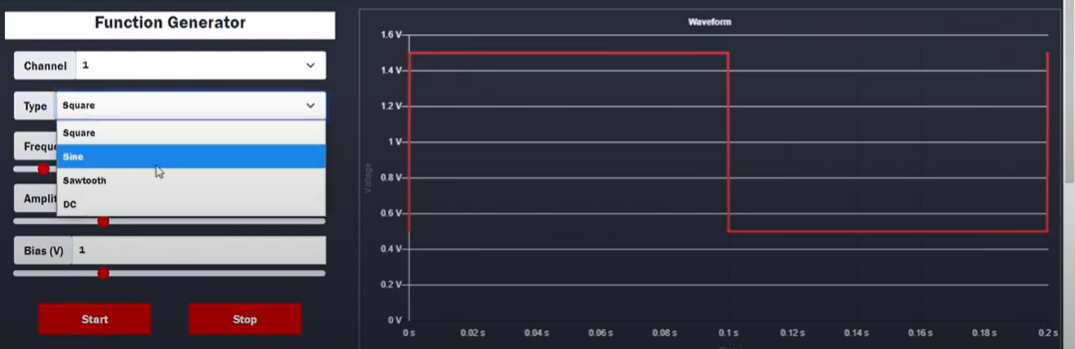
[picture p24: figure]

### 1.6.4. Logic Analyzer

The logic analyzer allows us to watch the changing of 8 bits simultaneously. You can turn on and off any channel you wish and can pause all 8 channels simultaneously. The logic analyzer does not trigger at this time and is planned for a future update. When the button is whited out, that means it is active, when red, that button is inactive.

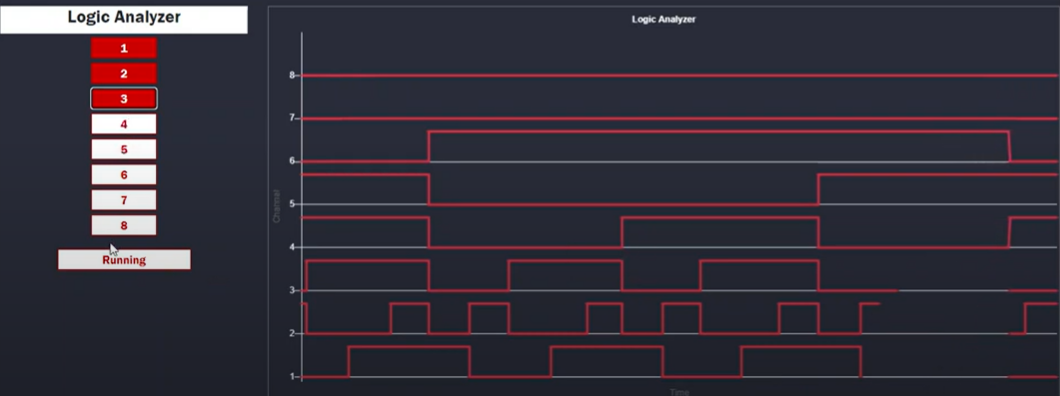
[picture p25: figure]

## 1.7. Data Acquisition: Multimeter

The four pins highlighted below are used to measure current, power, voltage, and resistance with the voltmeter. The ground pin is the ground reference for the VBUS pin. The VBUS pin is the measured voltage that is displayed in the GUI. VIN+ and VIN- are the current meter probes. Connect VIN+ to the positive side and VIN- to the negative side. Note: If you connect it backwards, the current will not read properly in the GUI. Negative current will be handled in a future update. The power is the current multiplied by the voltage, so if you want to measure power, you must measure the voltage and current in the same location.

The resistance measurement is not built into the multimeter and is instead calculated by ohm’s law with the current and voltage measurement. In order to measure the resistance of a resistor, you must measure the voltage across the resistor and the current through the resistor.

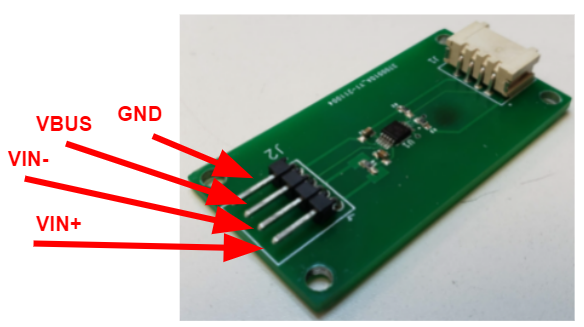
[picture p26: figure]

## 1.8. Data Acquisition: Oscilloscope

The photo below shows which wires are related to which parts of the oscilloscope. The oscilloscope is referenced to the TI Innovator Hub ground. The yellow wire is channel 1 and the white wire is channel 2. Once the wires are connected you can view the values using the oscilloscope GUI. The oscilloscope can only read values between 0V and 3V3. The red wire is not required, but can be used for 3V3 if needed. This red wire is limited to 100 mA.

## 1.9. Data Acquisition: Logic Analyzer

Pins 1-8 will read low when 0V is applied and high when 3V3 is applied. Voltages that are between 0V and 3V3 are undefined. Do not apply greater than 3V3. When nothing is applied to the pin it registers low. When using the logic analyzer each pin is referenced to ground.

## 1.10. Driving a Circuit: Function Generator

The function generator is operated from the function generator GUI. Using the image below, you connect a breadboard wire from whichever channel you want to use to where in your circuit you want the waveform applied too. All four channels can be hooked up simultaneously, but only one channel will operate at a time. The function generator channels are referenced to the ground pin shown below. The function generator can output signal voltages between 0V and 5V.

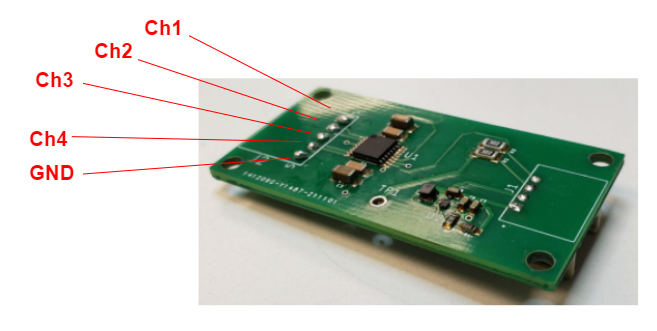
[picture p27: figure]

# 2. Additional Setup for Prototype (For Mark)

## 2.1. Introduction

This section of this document is meant to help those who are working behind the scenes with the unrefined product. As it stands, the TI Innovator HUB Data Acquisition Tool is still in its prototype stage. The user guide above shows how to operate the product. This section is meant for those with a deeper technical knowledge and those with the intention of further developing the product. This section covers how to set-up the device for the first time using Arduino and Code Composer Studio.

## 2.2. Setting up ESP32 Firmware (Arduino)

1. First we must flash the firmware to the ESP32 (wifi module). This is done via Arduino and this project was completed with Arduino 1.8.16 on Windows 10. Download and install Arduino.
2. Install ESP32 board via board manager. Follow this guide: ESP32 in Arduino (https://docs.espressif.com/projects/arduino-esp32/en/latest/installing.html).
3. You should now have this option in your board manager:

We chose to use DOIT ESP32 DEVKIT V1 because that is what our development board is.

4. Then you must install the ESPAsyncWebServer and AsyncTCP libraries in Arduino. These can be found at ESPAsyncWebServer (https://github.com/me-no-dev/ESPAsyncWebServer) and AsyncTCP github (https://github.com/me-no-dev/AsyncTCP). You will need to download the GitHub zip and install it. Use this guide: GitHub -> Arduino IDE (https://www.digikey.com/en/maker/blogs/2018/how-to-install-arduino-libraries).
5. Now, we will need to wire up the wifi module. Look at the image below:

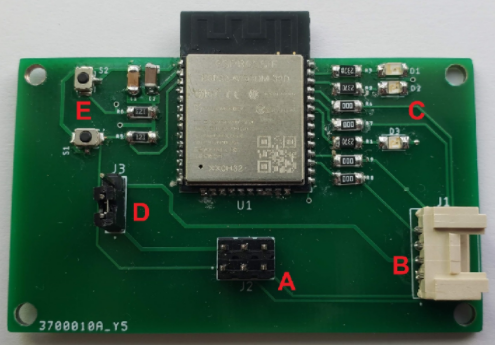
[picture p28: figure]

This is not the final iteration of the wifi PCB, make sure you are using the one that has only one grove connector. The PCB with two grove connectors is connected differently.

6. Connect a grove cable from B on the wifi PCB to the “OUT1” port on the TI Innovator HUB. This will provide a ground reference from the HUB.
7. Ensure that the jumper is on the bottom two pins at D on the wifi PCB.
8. Connect 3V3 from the HUB breadboard to the top left pin of the 2x3 male header at A on the wifi PCB.
9. Connect the programmer ground to the top middle pin at A on the wifi PCB.
10. Connect the programmer RX to the bottom middle pin at A on the wifi PCB. This pin goes to the ESP TX0.
11. Connect the programmer TX to the bottom left pin at A on the wifi PCB. This pin goes to the ESP RX0.
12. Power on the TI Innovator HUB.
13. It is assumed that the programmer drivers are installed and it is properly operating. Determine which COM port the programmer is using and then set the serial to that port in the Arduino IDE.
14. Optional: You can install a serial terminal and set it to 115200 baud to check the operation of the wifi module. A good serial terminal is Tera Term (https://ttssh2.osdn.jp/index.html.en). You should see a boot message when you press the lower push button (reset) at E on the wifi PCB. If you hold the upper push button (boot) while pressing the reset button, you should receive a “waiting for download” message. This means that the wifi module is in serial bootloader mode.

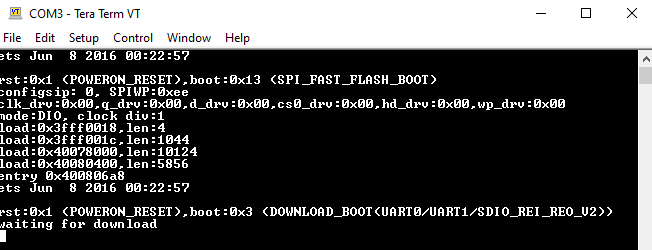
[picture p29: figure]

15. Now, the IDE should be configured and the programmer connected to the wifi module. Unfortunately we do not have any photos of the programmer connected to the wifi module.
16. If you have a serial terminal open, close it. The programmer cannot be used both in the serial terminal and by the Arduino IDE.
17. Open the esp32_firmware.ino sketch from the GitHub repository (Link (https://github.ncsu.edu/cedenni2/ti_82/tree/master/esp32_firmware)) and upload the sketch. You should see the image below:
18. If the ...___...___ does not stop, then press and hold the upper push button (boot) until it begins uploading, which will look like this:

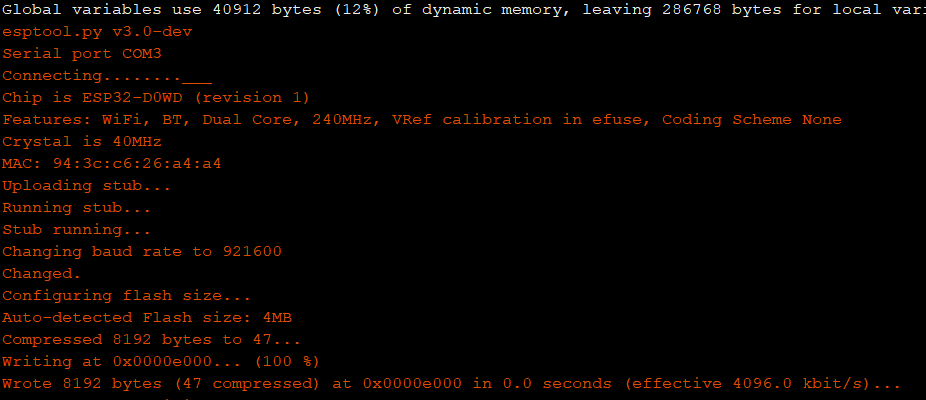
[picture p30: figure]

19. Once the upload is complete you will get this message:
20. Press the reset button and if you have a serial terminal, open it back up to view the ESP32. You should see the boot message along with the ESP32 IP address. The green LED will turn on after approximately 5 seconds. When the green LED is lit, check for an SSID called “ti82-team-12”. This means that the setup was successful.
21. If you receive an error when uploading, check the following:
  a. The COM port of the programmer is not being used by another program.
  b. The arduino IDE is set to the correct serial port.
  c. The programmer drivers are installed.
  d. The programmer is connected correctly.
  e. The ESP32 is receiving power from the TI HUB.
22. If the ...___...___ does not stop and pressing the boot button does not begin upload, check to make sure that the boot pin (GPIO-0) is going low when the push button is pressed. The pin to check is highlighted below:

## 2.3. Setting up MSP432P401R Firmware (Code Composer Studio)

1. The TI Innovator HUB is a MSP432P401R on the inside. Since the firmware is not a .hub sketch, as of right now the firmware must be flashed using code composer studio. This project was done using CCS 10.4.
2. Download and install code composer studio (CCS (https://www.ti.com/tool/CCSTUDIO)).
3. Follow this quickstart guide for the MSP432 and ensure that you can run a simple program on the device (Quickstart MSP432 (https://software-dl.ti.com/simplelink/esd/simplelink_msp432_sdk/1.40.01.00/docs/simplelink_mcu_sdk/Quick_Start_Guide.html)).
4. If not already installed, install the driverlib library (driverlib (https://www.ti.com/tool/MSPDRIVERLIB)).
5. Once CCS is installed, open CCS and import the project files at TI Innovator Hub Firmware (https://github.ncsu.edu/cedenni2/ti_82/tree/master/ti_innovator_hub_firmware/ti_hub_daq).

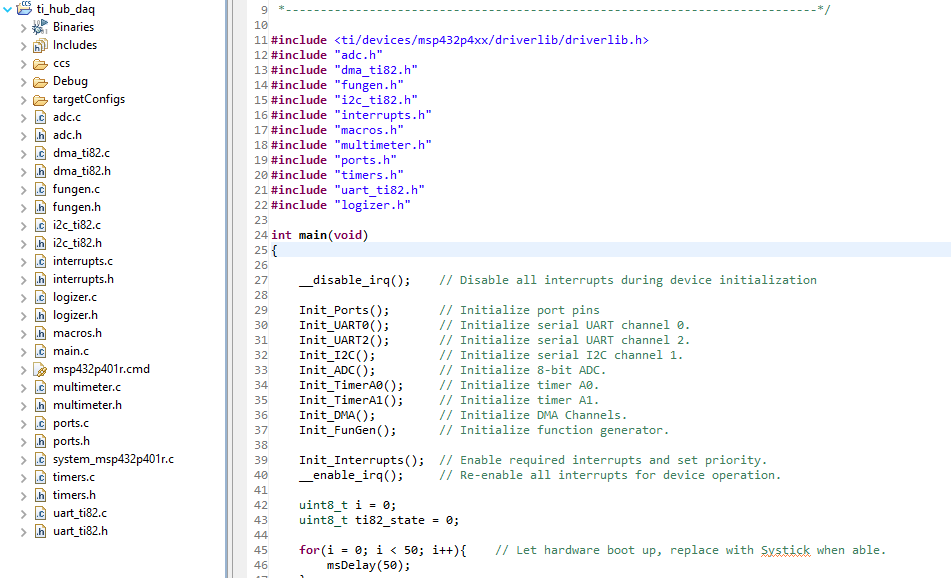
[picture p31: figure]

6. Connect the TI Innovator HUB using the microUSB port where it has PWR printed. You should have connected and tested it during the quickstart guide.
7. With the TI Innovator HUB connected, upload the program to the TI Innovator HUB. The TI Innovator HUB is now ready to be used with the modules.
8. If you need to revert the HUB back to its default firmware use this link (https://education.ti.com/en/software/details/en/EFD1D3762FE941FAA21E774D8520AEF0/TI-Innovator_Hub_Update_SW).
9. If you receive an error stating that the driverlib.h path could not be found, then the driverlib package is not installed correctly.

If you have downloaded the firmware for both the ESP32 and MSP432, wifi module and TI Innovator HUB, then you are ready to start the user guide.

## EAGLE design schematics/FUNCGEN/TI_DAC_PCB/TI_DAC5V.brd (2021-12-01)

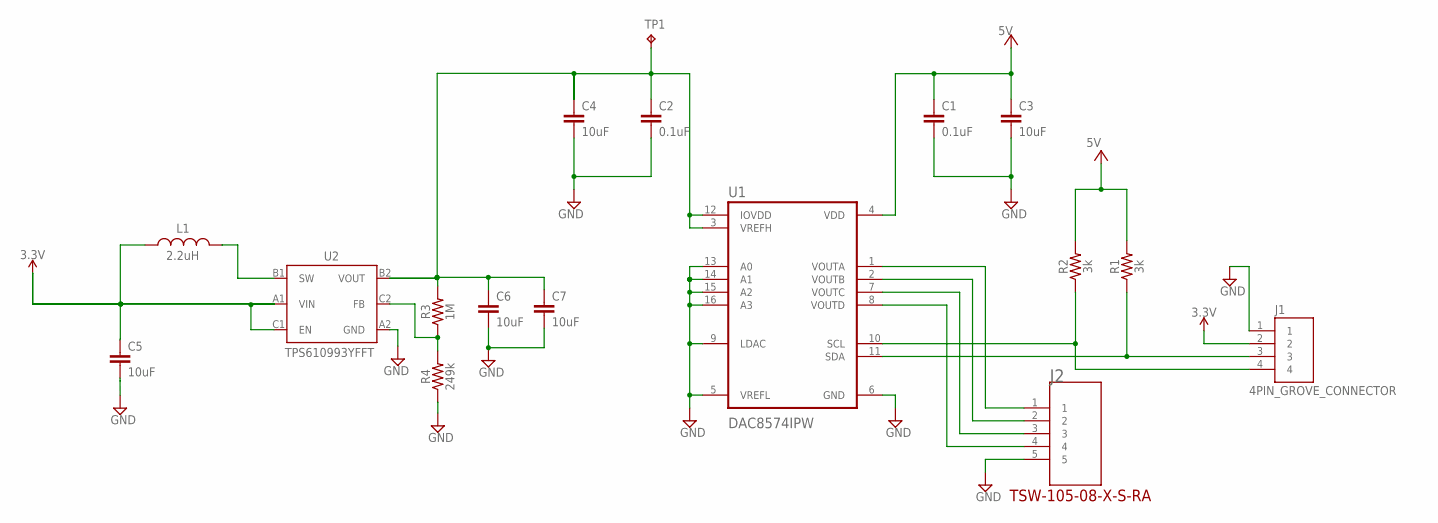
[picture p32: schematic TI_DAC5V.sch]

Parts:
C1, C2: 0.1uF; 1206
C3, C4: 10uF; 1206
C5, C6, C7: 10uF; CAPC1608X90N
J1: 4PIN_GROVE_CONNECTOR; SEEED_114020163
J2: TSW-105-08-X-S-RAJ; SAMTEC-TSW-105-08-X-S-RA
L1: 2.2uH; VLS201610CX-2R2M-1
R1, R2: 3k; 1206
R3: 1M; 0603
R4: 249k; 0603
TP1: TPPAD1-13; P1-13
U1: DAC8574IPW; SOP65P640X120-16N
U2: TPS610993YFFT

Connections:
3.3V: C5.1, J1.2, L1.1, U2.A1 (VIN), U2.C1 (EN)
5V: C1.1, C2.1, C3.1, C4.1, C6.1, C7.1, R1.2, R2.2, R3.2, TP1.TP, U1.3 (VREFH), U1.4 (VDD), U1.12 (IOVDD), U2.B2 (VOUT)
FB: R3.1, R4.2, U2.C2 (FB)
GND: C1.2, C2.2, C3.2, C4.2, C5.2, C6.2, C7.2, J1.1, J2.5, R4.1, U1.5 (VREFL), U1.6 (GND), U1.9 (LDAC), U1.13 (A0), U1.14 (A1), U1.15 (A2), U1.16 (A3), U2.A2 (GND)
SCL: J1.4, R2.1, U1.10 (SCL)
SDA: J1.3, R1.1, U1.11 (SDA)
SW: L1.2, U2.B1 (SW)
VOUTA: J2.1, U1.1 (VOUTA)
VOUTB: J2.2, U1.2 (VOUTB)
VOUTC: J2.3, U1.7 (VOUTC)
VOUTD: J2.4, U1.8 (VOUTD)

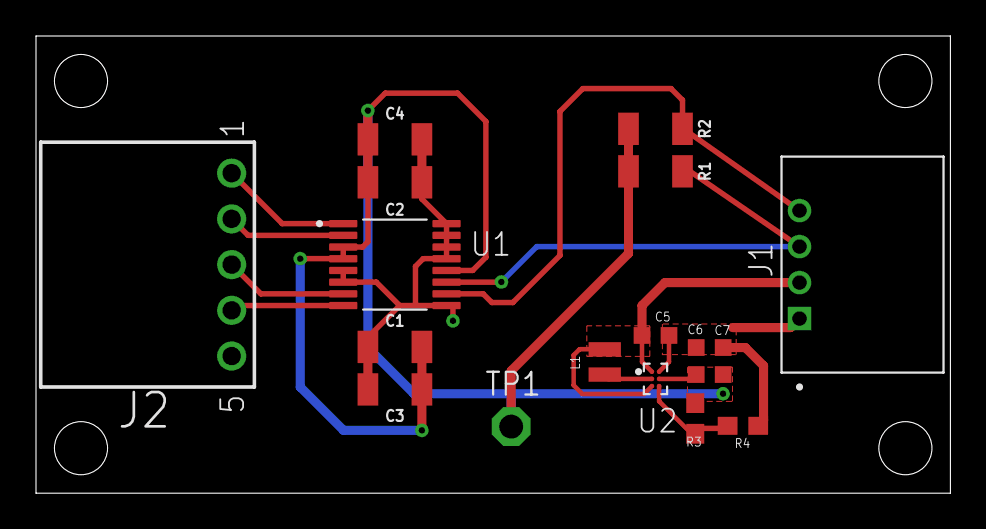
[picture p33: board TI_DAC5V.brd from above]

Board: 2 copper layers, 50.8 x 25.4 mm, 17 parts (0 on the bottom side), 11 nets.

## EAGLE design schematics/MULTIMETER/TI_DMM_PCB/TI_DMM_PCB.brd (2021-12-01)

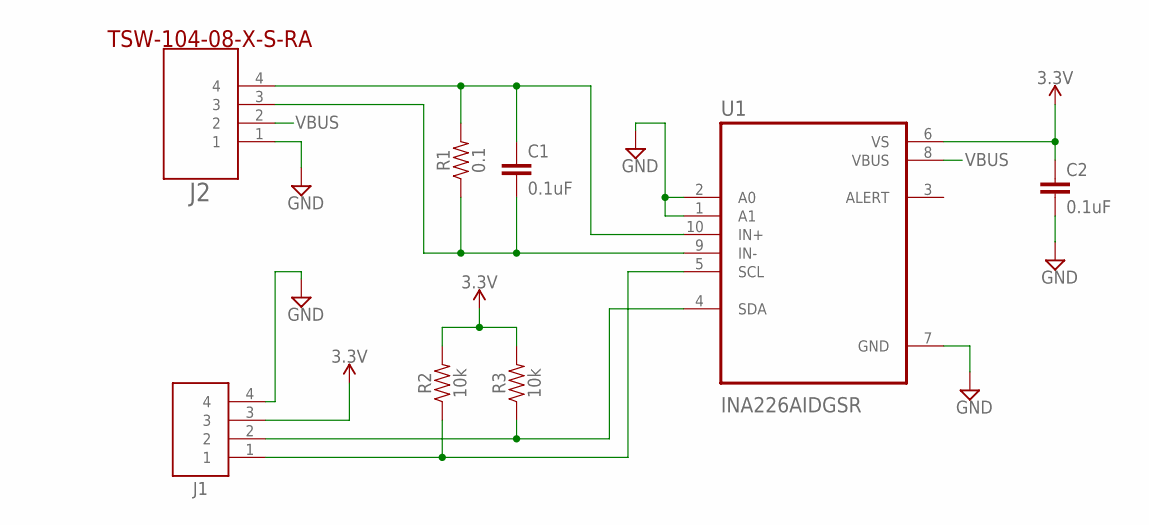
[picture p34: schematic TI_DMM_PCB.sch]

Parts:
C1, C2: 0.1uF; 0603
J1: 4PIN_GROVE_CONNECTOR; SEEED_114020163
J2: TSW-104-08-X-S-RAJ; SAMTEC-TSW-104-08-X-S-RA
R1: 0.1; 0603
R2, R3: 10k; 0603
U1: INA226AIDGSR; SOP50P490X110-10N

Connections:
3.3V: C2.1, J1.3, R2.2, R3.2, U1.6 (VS)
GND: C2.2, J1.4, J2.1, U1.1 (A1), U1.2 (A0), U1.7 (GND)
IN+: C1.1, J2.4, R1.2, U1.10 (IN+)
IN-: C1.2, J2.3, R1.1, U1.9 (IN-)
SCL: J1.1, R2.1, U1.5 (SCL)
SDA: J1.2, R3.1, U1.4 (SDA)
VBUS: J2.2, U1.8 (VBUS)

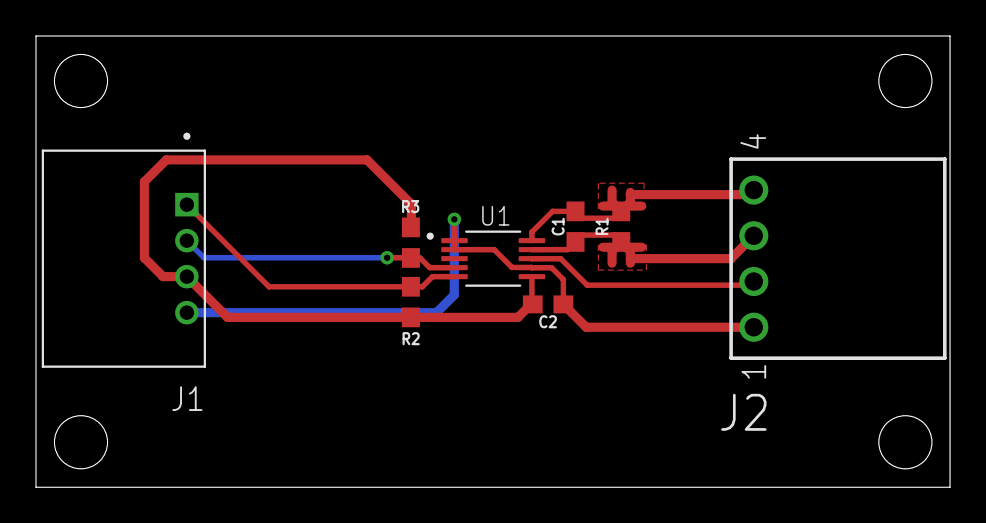
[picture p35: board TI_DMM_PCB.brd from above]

Board: 2 copper layers, 50.8 x 25.1 mm, 8 parts (0 on the bottom side), 7 nets.

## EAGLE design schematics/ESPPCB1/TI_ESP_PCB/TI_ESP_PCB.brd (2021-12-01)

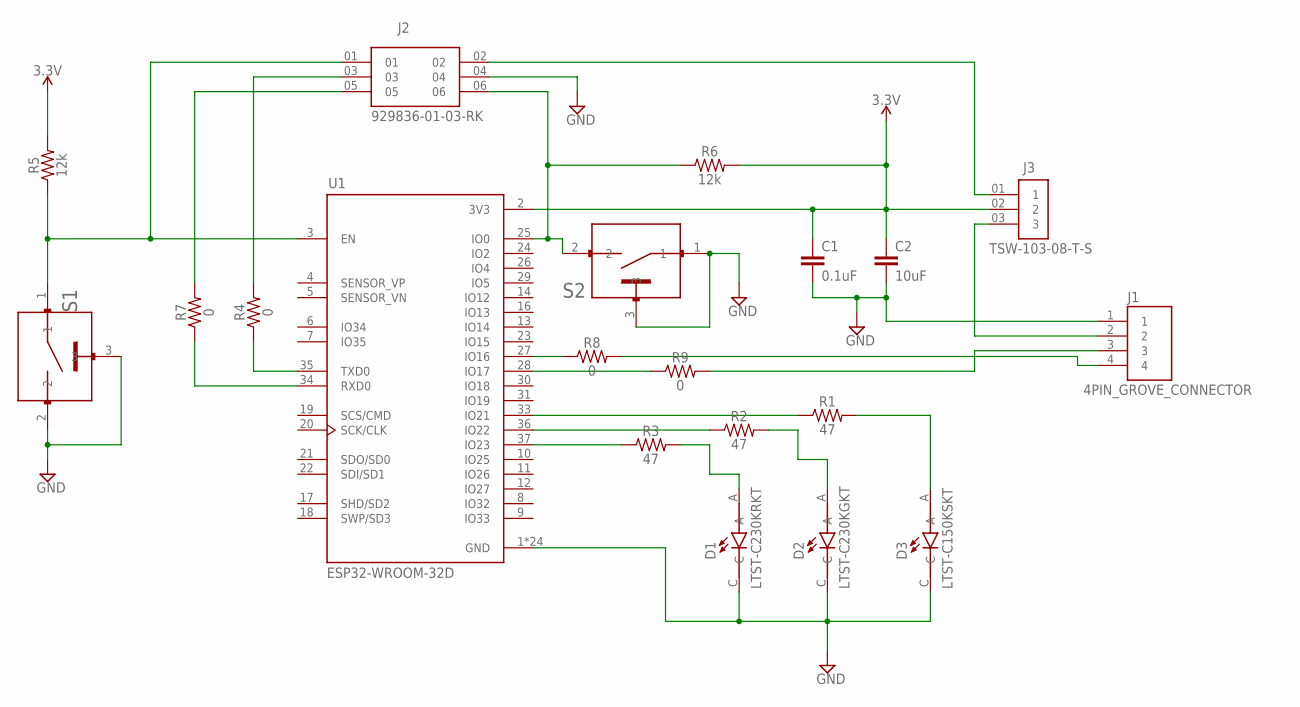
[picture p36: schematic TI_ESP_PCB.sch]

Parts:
C1: 0.1uF; 1206
C2: 10uF; 1206
D1: LTST-C230KRKT; LEDC3216X110
D2: LTST-C230KGKT; LEDC3216X110
D3: LTST-C150KSKT; LEDC3216X110
J1: 4PIN_GROVE_CONNECTOR; SEEED_114020163
J2: 929836-01-03-RK; 3M-2X3_6PIN_CONNECTOR
J3: TSW-103-08-T-S; SAMTEC_TSW-103-08-T-S
R1, R2, R3: 47; 1206
R4, R7, R8, R9: 0; 1206
R5, R6: 12k; 1206
S1, S2: B3U-1100P; SW_B3U-1100P
U1: ESP32-WROOM-32D; MODULE_ESP32-WROOM-32D

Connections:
3.3V: C1.1, C2.1, J3.02 (2), R5.2, R6.2, U1.2 (3V3)
EN: J2.01, R5.1, S1.1, U1.3 (EN)
GND: C1.2, C2.2, D1.C, D2.C, D3.C, J1.1, J2.04, S1.2, S1.3, S2.1, S2.3, U1.1 (GND), U1.15 (GND), U1.38 (GND), U1.39_1 (GND), U1.39_2 (GND), U1.39_3 (GND), U1.39_4 (GND), U1.39_5 (GND), U1.39_6 (GND), U1.39_7 (GND), U1.39_8 (GND), U1.39_9 (GND), U1.39_10 (GND), U1.39_11 (GND), U1.39_12 (GND), U1.39_13 (GND), U1.39_14 (GND), U1.39_15 (GND), U1.39_16 (GND), U1.39_17 (GND), U1.39_18 (GND), U1.39_19 (GND), U1.39_20 (GND), U1.39_21 (GND)
IO0: J2.06, R6.1, S2.2, U1.25 (IO0)
IO16: R8.1, U1.27 (IO16)
IO17: R9.1, U1.28 (IO17)
IO21: R1.1, U1.33 (IO21)
IO22: R2.1, U1.36 (IO22)
IO23: R3.1, U1.37 (IO23)
unnamed: J2.03, R4.2
unnamed: J1.2, J3.03 (3)
unnamed: J2.02, J3.01 (1)
unnamed: D1.A, R3.2
unnamed: D2.A, R2.2
unnamed: D3.A, R1.2
unnamed: J1.4, R8.2
unnamed: J1.3, R9.2
unnamed: J2.05, R7.2
RXD0: R7.1, U1.34 (RXD0)
TXD0: R4.1, U1.35 (TXD0)

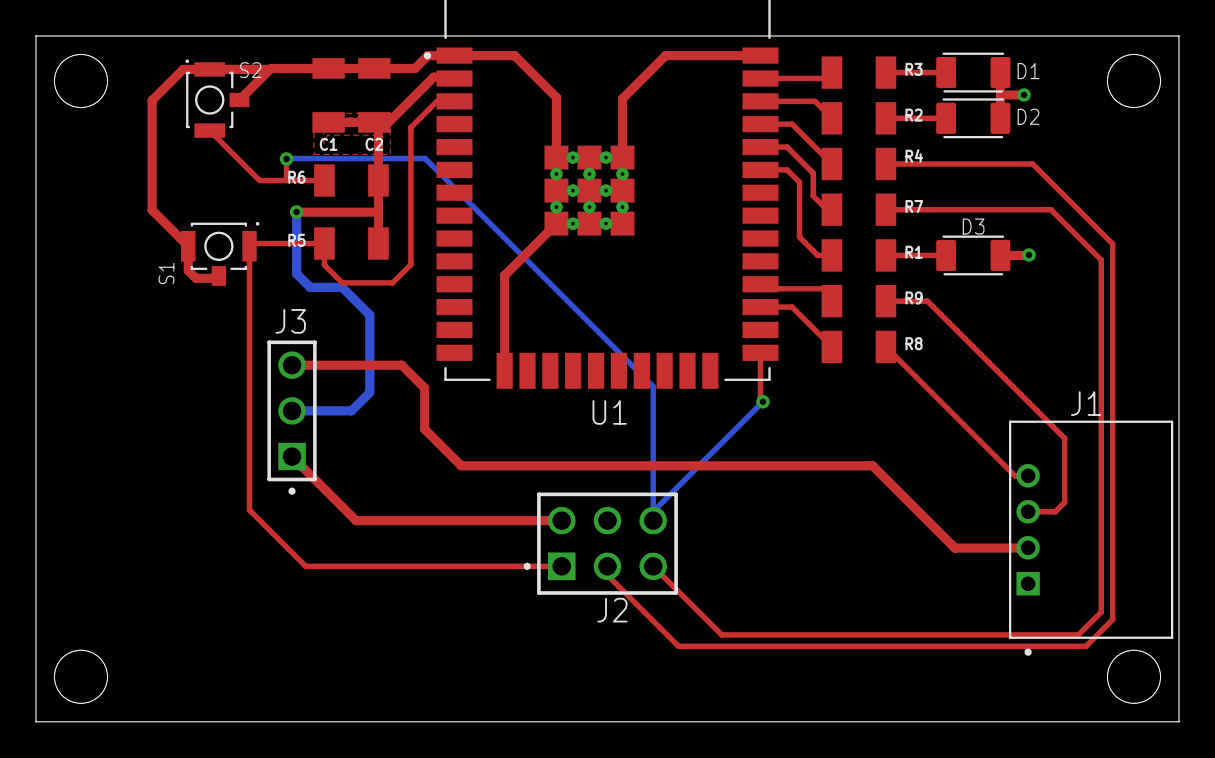
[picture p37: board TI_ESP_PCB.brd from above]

Board: 2 copper layers, 63.5 x 38.1 mm, 20 parts (0 on the bottom side), 20 nets.

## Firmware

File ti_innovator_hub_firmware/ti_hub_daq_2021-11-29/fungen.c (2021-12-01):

/*
 * fungen.c
 *
 *
 *  Command Mapping:
 *       9 - Type Ch1, 10 - Type Ch2, 11 - Type Ch3, 12 - Type Ch4
 *      13 - Amp  Ch1, 14 - Amp  Ch2, 15 - Amp  Ch3, 16 - Amp  Ch4
 *      17 - Freq Ch1, 18 - Freq Ch2, 19 - Freq Ch3, 20 - Freq Ch4
 *      21 - Bias Ch1, 22 - Bias Ch2, 23 - Bias Ch3, 24 - Bias Ch4
 *      25 - Duty Ch1, 26 - Duty Ch2, 27 - Duty Ch3, 28 - Duty Ch4
 *
 */

#include "macros.h"
#include "fungen.h"
#include "uart_ti82.h"

// Global Variables

// Default signal is the sine wave template.
uint16_t active_signal[128] = {20346, 20832, 21316, 21796, 22272, 22741, 23204, 23659, 24105, 24540, 24964, 25376, 25774, 26158, 26527, 26880,
                               27216, 27535, 27835, 28115, 28376, 28616, 28835, 29033, 29208, 29361, 29491, 29598, 29681, 29741, 29777, 29789,
                               29777, 29741, 29681, 29598, 29491, 29361, 29208, 29033, 28835, 28616, 28376, 28115, 27835, 27535, 27216, 26880,
                               26527, 26158, 25774, 25376, 24964, 24540, 24105, 23659, 23204, 22741, 22272, 21796, 21316, 20832, 20346, 19859,
                               19372, 18886, 18402, 17922, 17446, 16977, 16514, 16059, 15614, 15178, 14754, 14343, 13944, 13560, 13191, 12838,
                               12502, 12183, 11884, 11603, 11342, 11102, 10883, 10685, 10510, 10357, 10227, 10120, 10037,  9977,  9942,  9930,
                                9942,  9977, 10037, 10120, 10227, 10357, 10510, 10685, 10883, 11102, 11342, 11603, 11884, 12183, 12502, 12838,
                               13191, 13560, 13944, 14343, 14754, 15178, 15614, 16059, 16514, 16977, 17446, 17922, 18402, 18886, 19372, 19859};

uint16_t active_type = 1;
uint16_t active_amp  = 1;
uint16_t active_freq = 2;
uint16_t active_bias = 1;
uint8_t active_channel = CH_OFF; // Default is channel A

uint16_t fun_index = 0;

// 19859 is the anchor point for scaling and offset calculations.
uint16_t sine_template[128]     = {20346, 20832, 21316, 21796, 22272, 22741, 23204, 23659, 24105, 24540, 24964, 25376, 25774, 26158, 26527, 26880,
                                   27216, 27535, 27835, 28115, 28376, 28616, 28835, 29033, 29208, 29361, 29491, 29598, 29681, 29741, 29777, 29789,
                                   29777, 29741, 29681, 29598, 29491, 29361, 29208, 29033, 28835, 28616, 28376, 28115, 27835, 27535, 27216, 26880,
                                   26527, 26158, 25774, 25376, 24964, 24540, 24105, 23659, 23204, 22741, 22272, 21796, 21316, 20832, 20346, 19859,
                                   19372, 18886, 18402, 17922, 17446, 16977, 16514, 16059, 15614, 15178, 14754, 14343, 13944, 13560, 13191, 12838,
                                   12502, 12183, 11884, 11603, 11342, 11102, 10883, 10685, 10510, 10357, 10227, 10120, 10037,  9977,  9942,  9930,
                                    9942,  9977, 10037, 10120, 10227, 10357, 10510, 10685, 10883, 11102, 11342, 11603, 11884, 12183, 12502, 12838,
                                   13191, 13560, 13944, 14343, 14754, 15178, 15614, 16059, 16514, 16977, 17446, 17922, 18402, 18886, 19372, 19859};

uint16_t square_template[128]   = {29842, 29842, 29842, 29842, 29842, 29842, 29842, 29842, 29842, 29842, 29842, 29842, 29842, 29842, 29842, 29842,
                                   29842, 29842, 29842, 29842, 29842, 29842, 29842, 29842, 29842, 29842, 29842, 29842, 29842, 29842, 29842, 29842,
                                   29842, 29842, 29842, 29842, 29842, 29842, 29842, 29842, 29842, 29842, 29842, 29842, 29842, 29842, 29842, 29842,
                                   29842, 29842, 29842, 29842, 29842, 29842, 29842, 29842, 29842, 29842, 29842, 29842, 29842, 29842, 29842, 29842,
                                    9966,  9966,  9966,  9966,  9966,  9966,  9966,  9966,  9966,  9966,  9966,  9966,  9966,  9966,  9966,  9966,
                                    9966,  9966,  9966,  9966,  9966,  9966,  9966,  9966,  9966,  9966,  9966,  9966,  9966,  9966,  9966,  9966,
                                    9966,  9966,  9966,  9966,  9966,  9966,  9966,  9966,  9966,  9966,  9966,  9966,  9966,  9966,  9966,  9966,
                                    9966,  9966,  9966,  9966,  9966,  9966,  9966,  9966,  9966,  9966,  9966,  9966,  9966,  9966,  9966,  9966};

uint16_t saw_template[128]      = { 9948, 10102, 10258, 10412, 10568, 10722, 10878, 11032, 11188, 11342, 11498, 11652, 11808, 11962, 12118, 12272,
                                   12428, 12582, 12738, 12892, 13048, 13202, 13358, 13512, 13668, 13822, 13978, 14132, 14288, 14442, 14598, 14752,
                                   14908, 15062, 15218, 15372, 15528, 15682, 15838, 15992, 16148, 16302, 16458, 16612, 16768, 16922, 17078, 17232,
                                   17388, 17542, 17698, 17852, 18008, 18162, 18318, 18472, 18628, 18782, 18938, 19092, 19248, 19402, 19558, 19712,
                                   19868, 20022, 20178, 20332, 20488, 20642, 20798, 20952, 21108, 21262, 21418, 21572, 21728, 21882, 22038, 22192,
                                   22348, 22502, 22658, 22812, 22968, 23122, 23278, 23432, 23588, 23742, 23898, 24052, 24208, 24362, 24518, 24672,
                                   24828, 24982, 25138, 25292, 25448, 25602, 25758, 25912, 26068, 26222, 26378, 26532, 26688, 26842, 26998, 27152,
                                   27308, 27462, 27618, 27772, 27928, 28082, 28238, 28392, 28548, 28702, 28858, 29012, 29168, 29322, 29478, 29632};


void Init_FunGen(void){

    int i = 0;
    for(i = 0; i < 4; i++){
        Set_Command_Value(9 + i, 0);
        Set_Command_Value(13+ i, 19859);
        Set_Command_Value(21+ i, 19859);
        Set_Command_Value(17+ i,  5859);
    }
}


uint8_t FunGen_Process(void){

    if((active_channel == CH_OFF) || !Is_I2C_Ready()){
        return 1;
    }
    if(active_channel & 0x20){
        uint8_t packet[3] = {(active_channel & 0x1F), 0x00, 0x00};
        I2C1_TX_RX(0x4C, packet, 3, FALSE);
    } else{
        uint8_t packet[3] = {active_channel, (active_signal[fun_index] >> 8), active_signal[fun_index]};
        I2C1_TX_RX(0x4C, packet, 3, FALSE);
        fun_index = (fun_index + 1) % 128;
    }
    return 0;
}

void Update_Signal_Array(void){

    TIMER_A0->CCTL[0] &= ~0x10;      // Disable compare value interrupt for channel 0

    Set_Active_Channel(Get_Command_Value(5));
    int16_t channel_value = ((0x1F & Get_Command_Value(5)) / 2) - 8;
    if(channel_value < 0){
        return;
    }
    Set_Active_Type(Get_Command_Value(9 + channel_value));
    Set_Active_Bias(Get_Command_Value(21 + channel_value));
    Set_Active_Amp(Get_Command_Value(13 + channel_value));
    Set_Timer_Frequency(Get_Command_Value(17 + channel_value));

    uint16_t i = 0;
    int32_t temp = 0;

    // Compiler raises warning if declared inside switch statement.
    int32_t bias = 0;
    float amp_scale = 0.0;
    int32_t amp = 0;

    switch(active_type){
    case 0:                 // Square Wave
        bias = active_bias - 19895;
        amp_scale = active_amp*(3.3/65535);
        amp  = 0;
        for(i = 0; i < 128; i++){
            amp  = (int32_t)((amp_scale*2*(square_template[i] - 19895))/2);
            temp = 19895 + bias + amp;
            if(temp > 65535){
                temp = 65535;
            } else if(temp < 0){
                temp = 0;
            }
            active_signal[i] = temp;
        }
        break;
    case 1:                 // Sine Wave is option 1.
        bias = active_bias - 19895;
        amp_scale = active_amp*(3.3/65535);
        amp  = 0;
        for(i = 0; i < 128; i++){
            amp  = (int32_t)((amp_scale*2*(sine_template[i] - 19895))/2);
            temp = 19895 + bias + amp;
            if(temp > 65535){
                temp = 65535;
            } else if(temp < 0){
                temp = 0;
            }
            active_signal[i] = temp;
        }
        break;
    case 2:
        bias = active_bias - 19895;
        amp_scale = active_amp*(3.3/65535);
        amp  = 0;
        for(i = 0; i < 128; i++){
            amp  = (int32_t)((amp_scale*2*(saw_template[i] - 19895))/2);
            temp = 19895 + bias + amp;
            if(temp > 65535){
                temp = 65535;
            } else if(temp < 0){
                temp = 0;
            }
            active_signal[i] = temp;
        }
        break;
    case 3:                 // DC Wave
        for(i = 0; i < 128; i++){
            active_signal[i] = active_bias;
        }
        // Add code to set longer period for DC.
        break;
    default:
        break;
    }

    TIMER_A0->CCTL[0] |=  0x10;      // Enable compare value interrupt for channel 0
}

void Set_Active_Channel(uint8_t value){
    active_channel = value;
}

void Set_Active_Type(uint16_t value){
    active_type = value;
}

void Set_Active_Bias(float value){

    active_bias = (uint16_t)(value);
}

void Set_Active_Amp(float value){

    active_amp  = (uint16_t)(value);
}

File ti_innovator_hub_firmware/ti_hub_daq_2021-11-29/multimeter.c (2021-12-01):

/*
 * multimeter.c
 *
 * Description: INA226, used to measure voltage, current, and power. Can be setup to
 *              measure resistance.
 *
 *    Registers   00h Configuration   - R/W
 *                01h Shunt Voltage   - R       2.5 uV/bit
 *                02h Bus Voltage     - R       1.25 mV/bit
 *                03h Power           - R       25*(Current_LSB) W/bit
 *                04h Current         - R       Current_LSB A/bit
 *                05h Calibration     - R/W
 *
 * Note 1: The I2C that we are using is on pins 9(P6_5/SCL) and 10(P6_4/SDA).
 *
 * Note 2: INA226 booster address is h40. May be different, depending on A0 and A1 wiring.
 *         The address is h40 for the TI DAQ project, with A0 and A1 grounded.
 *
 */

#include <ti/devices/msp432p4xx/driverlib/driverlib.h>
#include "dma_ti82.h"
#include "macros.h"
#include "uart_ti82.h"

    //Calibrate_Multimeter(DMM_CAL_VAL);    // Only needed for DMM.
    //while(!Is_I2C_Ready());
    //Configure_Multimeter(DMM_CONF_VAL);
int     bus_voltage = 0;
int     dmm_state = 0;
int     dmm_values[5] = {0, 0, 0, 0, 0};
char    dmm_value_select = 0; // 0 - Shunt, 1 - Bus, 2 - Power, 3 - Current, 4 - Unused
uint8_t dmm_blob[7] = {4, 0, 0, 0, 0, 0, 0};
uint16_t dmm_len = 7;

// Move to separate header file.
extern volatile char tx1_done;
extern volatile char tx2_done;

/*
 * This function writes to the calibration register. Returns 1 if unsuccessful,
 * returns 0 if calibration starts. Give it a 16b input.
 *
 */
int Calibrate_Multimeter(unsigned int calibrate_value){

    if(!Is_I2C_Ready()){    // I2C is not available, return 1
        return 1;
    }

    unsigned char bytes[3] = {CAL_REG, 0x00, 0x00}; // Set up I2C write data
    bytes[1] = (calibrate_value >> 8) & 0xFF;       // Send MSB then LSB
    bytes[2] = calibrate_value & 0xFF;

    I2C1_TX_RX(DMM_ADDR, bytes, 3, 0);              // Kick off I2C write

    return 0;
}

int Configure_Multimeter(unsigned int configure_value){

    if(!Is_I2C_Ready()){    // I2C is not available, return 1
        return 1;
    }

    unsigned char bytes[3] = {CONF_REG, 0x00, 0x00}; // Set up I2C write data
    bytes[1] = (configure_value >> 8) & 0xFF;       // Send MSB then LSB
    bytes[2] = configure_value & 0xFF;

    I2C1_TX_RX(DMM_ADDR, bytes, 3, 0);              // Kick off I2C write

    return 0;
}

/*
 * This function reads value at the specified register. If I2C is busy or
 * if given an incorrect register value, returns 1. If I2C read is started,
 * returns 0. Give it one of these options: SHUNTV, BUSV, POWER, CURRENT.
 *
 */
int Read_Multimeter_Value(unsigned char this_register){

    if(!Is_I2C_Ready()){    // I2C is not available, return 1
        return 1;
    }

    unsigned char bytes[] = {0x00};

    switch(this_register){
    case SHUNTV:
        dmm_value_select = 0;
        bytes[0] = SHUNT_REG;
        I2C1_TX_RX(DMM_ADDR, bytes, 1, 1);
        return 0;
    case BUSV:
        dmm_value_select = 1;
        bytes[0] = BUS_REG;
        I2C1_TX_RX(DMM_ADDR, bytes, 1, 1);
        return 0;
    case POWER:
        dmm_value_select = 2;
        bytes[0] = POWER_REG;
        I2C1_TX_RX(DMM_ADDR, bytes, 1, 1);
        return 0;
    case CURRENT:
        dmm_value_select = 3;
        bytes[0] = CURRENT_REG;
        I2C1_TX_RX(DMM_ADDR, bytes, 1, 1);
        return 0;
    default:
        return 1;
    }
}

// ["0x0000","0x0000","0x0000"]
// 0123456789012345678901234567   4567, 13 14 15 16, 22 23 24 25
void Json_Dmm_Str(void){

    char hexStr[32];
    int  tempVal = 0;
    int i = 0;
    int j = 0;

    for(i = 0; i < 32; i++){
        hexStr[i] = '\0';
    }

    hexStr[0] = '[';
    hexStr[1] = '\"';
    hexStr[2] = '0';
    hexStr[3] = 'x';
    hexStr[8] = '\"';
    hexStr[9] = ',';
    hexStr[10] = '\"';
    hexStr[11] = '0';
    hexStr[12] = 'x';
    hexStr[17] = '\"';
    hexStr[18] = ',';
    hexStr[19] = '\"';
    hexStr[20] = '0';
    hexStr[21] = 'x';
    hexStr[26] = '\"';
    hexStr[27] = ']';
    hexStr[28] = 'p';
    //hexStr[29] = '\r';
    //hexStr[30] = '\n';

    j = 4;
    for(i = 3; i >= 0; i--){
        tempVal = (dmm_values[1] >> (4*i)) & 0xF; // Bus
        if(tempVal <= 9){
            hexStr[j] = tempVal + 48;
        }
        else{
            hexStr[j] = tempVal + 55;
        }

        tempVal = (dmm_values[3] >> (4*i)) & 0xF; // Current
        if(tempVal <= 9){
            hexStr[j+9] = tempVal + 48;
        }
        else{
            hexStr[j+9] = tempVal + 55;
        }

        tempVal = (dmm_values[2] >> (4*i)) & 0xF; // Power
        if(tempVal <= 9){
            hexStr[j+18] = tempVal + 48;
        }
        else{
            hexStr[j+18] = tempVal + 55;
        }
        j++;

    }
    TX_Debug(hexStr);
}


void Multimeter_Process(void){

    TIMER_A0->CCTL[0] &= ~0x10;      // Disable compare value interrupt for channel 0
    int i = 0;
    for(i = 0; i < 10; i++){    // Let hardware boot up, replace with systick when able.
        msDelay(1);
    }
    // Code for DMM.
    switch(dmm_state){
    case 0:
        Read_Multimeter_Value(BUSV);
        dmm_blob[2] = dmm_values[1] & 0xFF;
        dmm_blob[1] = (dmm_values[1] & 0xFF00) >> 8;
        dmm_state = 1;
        break;
    case 1:
        Read_Multimeter_Value(CURRENT);
        dmm_blob[4] = dmm_values[3] & 0xFF;
        dmm_blob[3] = (dmm_values[3] & 0xFF00) >> 8;
        dmm_state = 2;
        break;
    case 2:
        Read_Multimeter_Value(POWER);
        dmm_blob[6] = dmm_values[2] & 0xFF;
        dmm_blob[5] = (dmm_values[2] & 0xFF00) >> 8;
        dmm_state = 0;
        break;
    default:
        break;
    }

    for(i = 0; i < 10; i++){    // Let hardware boot up, replace with systick when able.
        msDelay(1);
    }
    TIMER_A0->CCTL[0] |=  0x10;      // Enable compare value interrupt for channel 0

    Dma_Ch4_Uart2_Send_String(dmm_blob, dmm_len);
}

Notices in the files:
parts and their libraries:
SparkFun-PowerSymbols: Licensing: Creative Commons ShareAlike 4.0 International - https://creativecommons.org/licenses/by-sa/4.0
